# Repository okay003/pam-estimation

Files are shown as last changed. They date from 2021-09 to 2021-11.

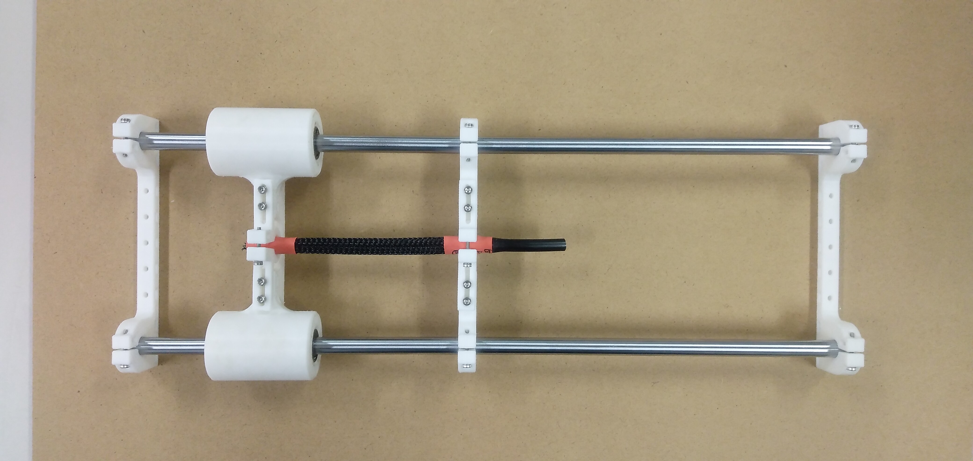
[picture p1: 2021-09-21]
overview.jpg

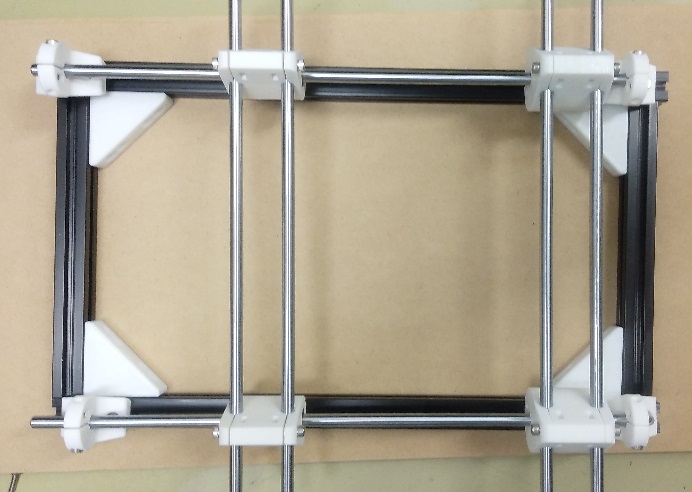
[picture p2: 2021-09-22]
temp state.jpg

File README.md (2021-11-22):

# pam-estimation

空気圧人工筋肉（PAM）を評価するための設備です。  
圧力を入力、その際の変位と収縮力を出力として計測します。  

概観
overview

試作版
oldsys

PAMの吸排気端を固定し、自由端が軸方向に直線的に収縮できるよう、リニアベアリング付きのガイドを配置してあります。  
計測のメインターゲットである変位はレーザ変位計VL53L0Xを用いて計測し、ArduinoとProcessingを介してPCでデータ処理を行います。  
収縮力は重りを用いて計測します。  
重りによる収縮力の計測は分解能が低く、システムによっては評価として不十分となるため、将来的にはエアシリンダ等を用いて負荷を連続的に制御できるようにします。  

研究で必要になったため開発しています。  

### BOM
・4本　任意長のアルミフレーム（ミスミ 5シリーズ）  
・32個　M4アルミフレーム用ナット  
・32個　M4六角穴付ボルト  
・6本　M8シャフト（アルミフレームと同じ長さ）  
・2個　M8リニアベアリング  
・1個　レーザ変位計 VL53L0X  
・1個　Arduino UNO  
・1本　Arduino用USBケーブル  
・1台　処理用PC  
・コンプレッサ  
・制御弁  
・PAM  
・計測用の重り

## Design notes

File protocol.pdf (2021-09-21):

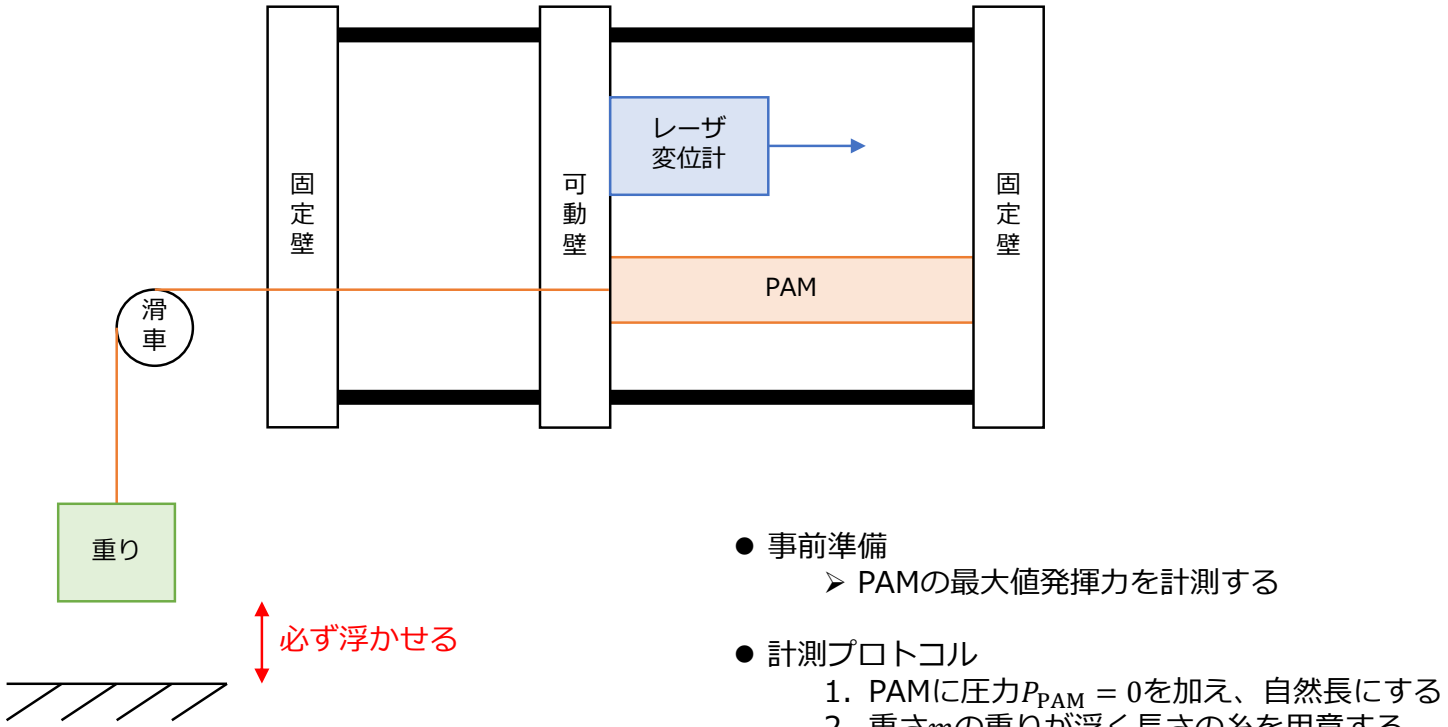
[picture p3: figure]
⚫ 事前準備 ➢ PAMの最大値発揮力を計測する; ⚫ 計測プロトコル 1. PAMに圧力PPAM = 0を加え、自然長にする; PAM; レーザ 変位計; 必ず浮かせる

2. 重さmの重りが浮く長さの糸を用意する
3. レーザ変位計が読んだ距離Lを計測する
4. PAMに圧力PPAMを加え、漸増させる（その結果、可動壁がPAMに牽引され移動する）
5. レーザ変位計が読んだ距離L

′を計測する
6. 圧力PPAMにおけるPAMの変位を、L − L

′より算出し、記録する
7. PAMに加える圧力PPAMを大まかに（1 [V]ずつ？）昇圧し、再度3.-10.を実行する
8. 実際に使いたい区間もしくは非線形性が著しい区間がある場合、 その区間に対してPAMに加える圧力PPAMを細かく（0.1 [V]ずつ？）昇圧し、再度3.-10.を実行 する
9. 重りの重さmを変更し、再度1.-8.を実行する 10.同規格のPAMや別規格のPAMに対して、再度1.-12.を実行する

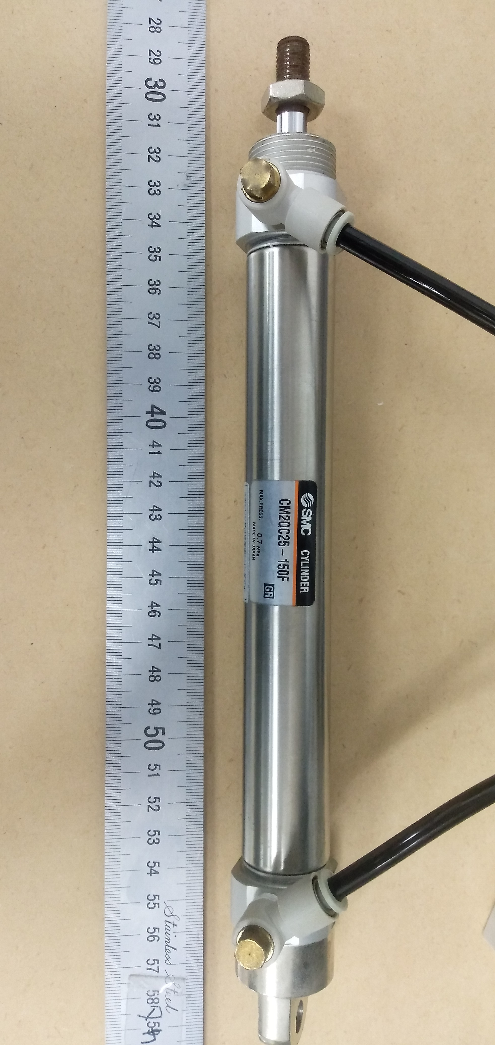
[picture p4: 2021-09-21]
aircylinder.jpg

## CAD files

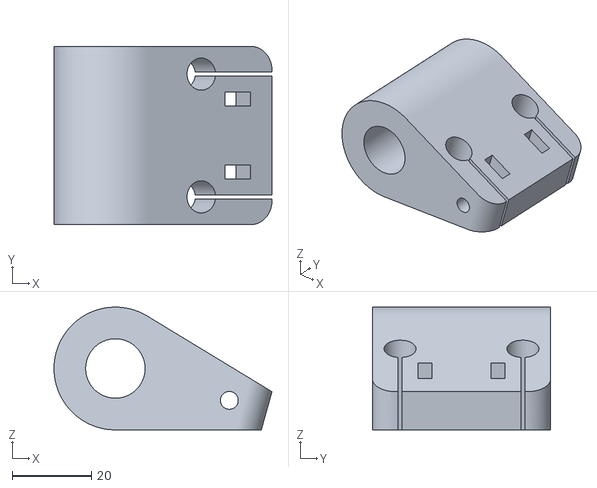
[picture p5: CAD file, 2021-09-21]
stl/slide holder.stl
55.0 x 45.0 x 31.0

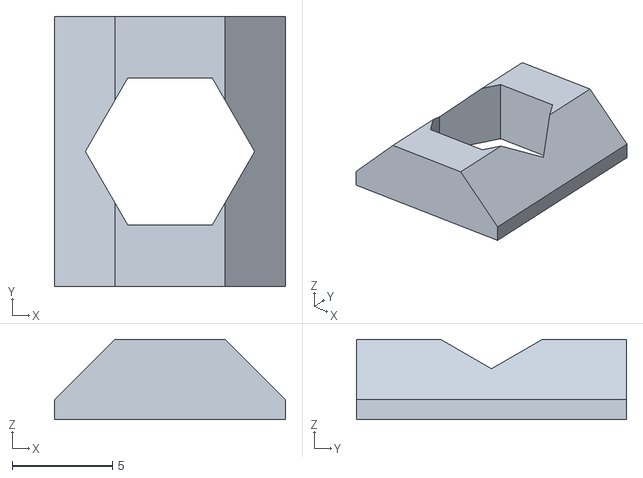
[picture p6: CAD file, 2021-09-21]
stl/key.stl
11.5 x 13.4 x 4.00

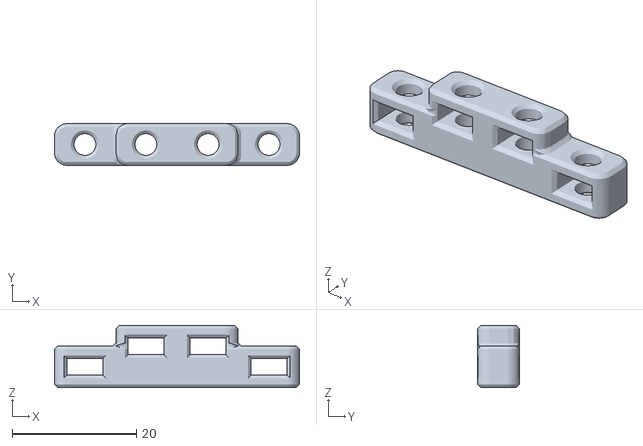
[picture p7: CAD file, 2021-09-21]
stl/vl53l0x holder.stl
39.4 x 6.70 x 10.0

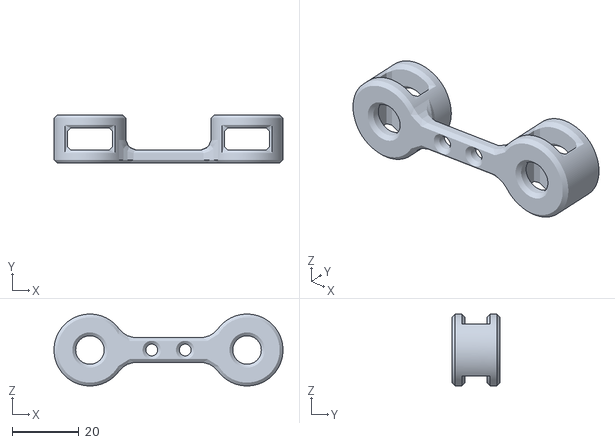
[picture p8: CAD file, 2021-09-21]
stl/vl53l0x calibratior.stl
68.5 x 14.5 x 21.5

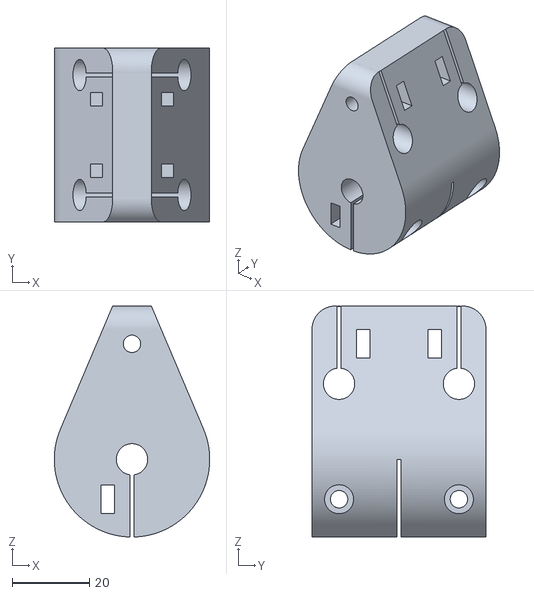
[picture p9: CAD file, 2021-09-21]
stl/hold holder.stl
40.2 x 45.0 x 59.8

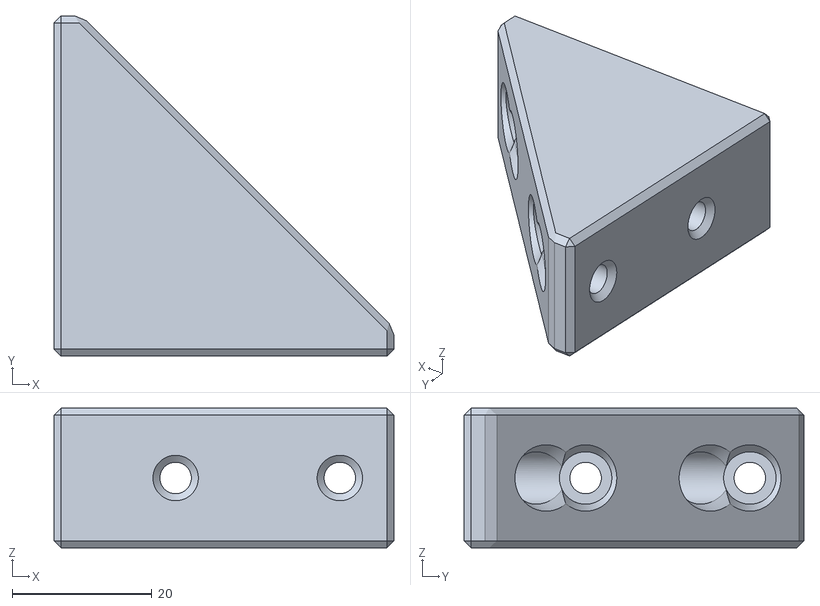
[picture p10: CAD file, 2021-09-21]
stl/elbow.stl
48.7 x 48.7 x 20.0

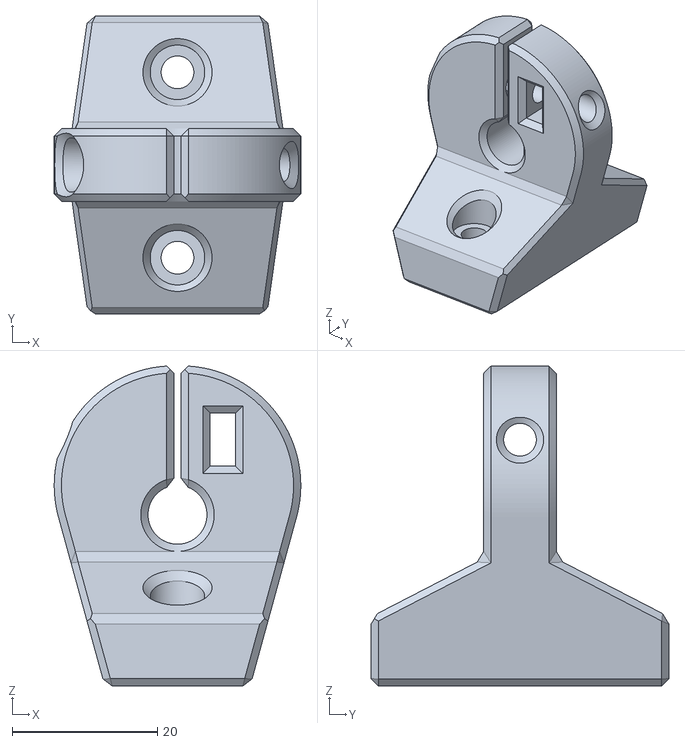
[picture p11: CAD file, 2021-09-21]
stl/shaft holder.stl
33.9 x 41.0 x 44.0

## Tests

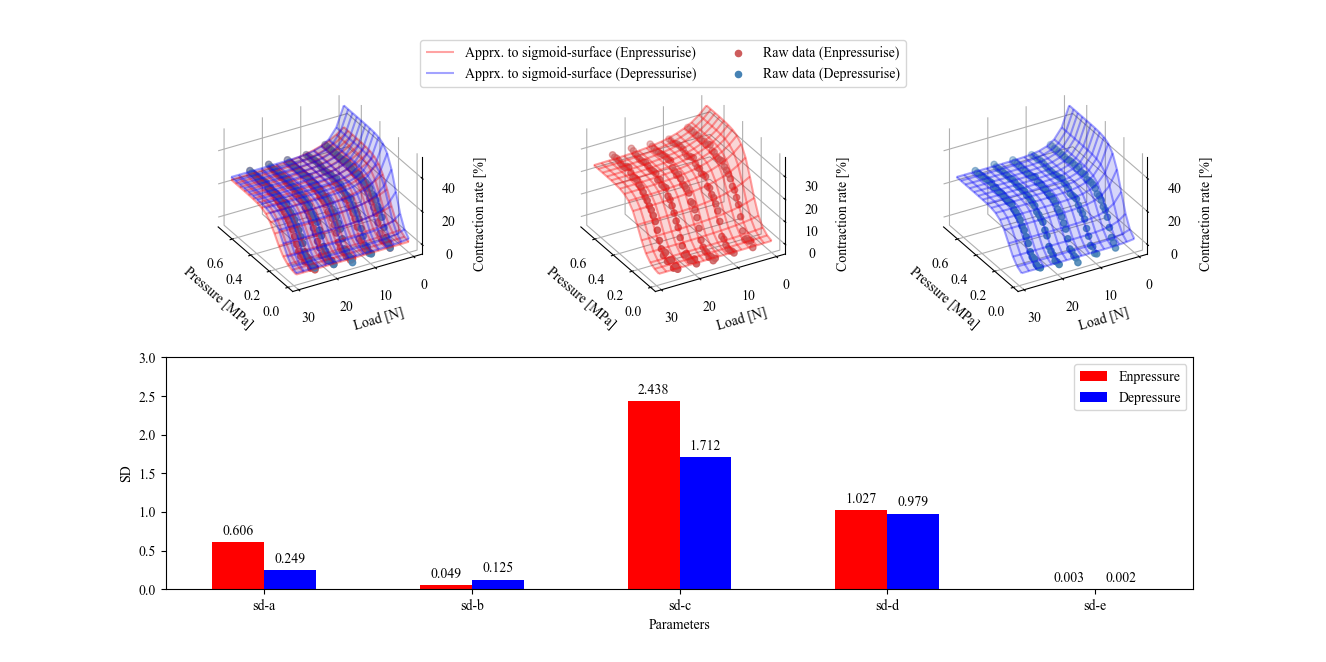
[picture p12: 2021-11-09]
fig/test.png

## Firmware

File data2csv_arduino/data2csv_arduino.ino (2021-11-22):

#include <VL53L0X.h>
#include <Wire.h>

VL53L0X sensor;
uint8_t MCP4725_ADDRESS = 0x60;  // mcp4725 address

// get distance data from VL53L0X
int getDistance();
// set DAC-out voltage
void setDac(uint16_t target);
// serial communication, send to processing
void scA2P(int index);
// wave initialize routine
void waveInitialize();
// wave finalize routine
void waveFinalize();

const String serialNumber = "MonoPlaE";  // default serialNumber is A
const int mass = 2500;  // default mass is 99 [g]
int eprVin = 0;  // default eprVin is 0
const int freeLength = 234;

float distanceAverage = 0;
int averageCounter = 0;

#define RISE_HOLD 0
#define RISE 1
#define FALL 2
#define FALL_HOLD 3
#define END 999
int waveState = RISE_HOLD;  // sequencer for PAM input
int waveCounter = 0;  // counter for PAM input

bool isFirst = true;

int stepNum = 1 << 5; // resolution of PAM input
int stepHeight = 4096 / stepNum; // PAM input value per step
unsigned long holdTimer = 0;  // timer of hold section
int holdTime = 8000; // length of hold section
int slope = 1; // speed of PAM input

void setup() {
  delay(4000);
  
  Serial.begin(9600);

  Wire.begin();
  sensor.setTimeout(500);
  if (!sensor.init()) {
    Serial.println("Failed to detect and initialize VL53L0X");
    while (1) {}
  }
  sensor.startContinuous();

  holdTimer = millis();
}

void loop() {
  setDac(eprVin);

  int cut = stepHeight * waveCounter - 1;
  if (waveCounter > stepNum) {
    cut = stepHeight * (2 * stepNum - waveCounter) - 1;
  }
  if (cut < 0) {
    cut = 0;
  }

  if (isFirst) {
    waveInitialize();
    isFirst = false;
  }

  switch (waveState) {
    case RISE_HOLD: // hold section (rise)
      if (millis() - holdTimer < holdTime) {
        if (waveCounter == 0) {
          eprVin = 0;
        } else {
          eprVin = cut;
        }
        distanceAverage += getDistance();
        averageCounter++;
      } else if (waveCounter == stepNum) {  // waveCounter gets turning point
        waveFinalize();
        waveState = FALL;
      } else {
        waveFinalize();
        waveState = RISE;
      }
      break;
    case RISE: // rise section
      if (eprVin < cut) {
        eprVin += slope;
        delay(10);
        if (eprVin > cut) {
          eprVin = cut;
        }
      } else {
        waveState = RISE_HOLD;
        holdTimer = millis();
      }
      break;
    case FALL_HOLD: // hold section (fall)
      if (millis() - holdTimer < holdTime) {
        eprVin = cut;
        distanceAverage += getDistance();
        averageCounter++;
      } else if (waveCounter == 2 * stepNum) {
        waveFinalize();
        waveState = END;
      } else {
        waveFinalize();
        waveState = FALL;
      }
      break;
    case FALL: // fall section
      if (eprVin > cut + 1) {
        eprVin -= slope;
        delay(10);
        if (eprVin < cut) {
          eprVin = cut;
        }
      } else {
        waveState = FALL_HOLD;
        holdTimer = millis();
      }
      break;
    case END: // end section
      scA2P();
      Serial.end();
      break;
    default:
      while (1) {
        Serial.println("error");
        delay(100);
      }
      break;
  }
  if (eprVin < 0) {
    eprVin = 0;
  }
}

// get distance data from VL53L0X
int getDistance() {
  int dist = sensor.readRangeContinuousMillimeters();
  if (sensor.timeoutOccurred()) {
    Serial.print("VL53L0X is timeouted");
  }
  return dist;
}

// set DAC-out voltage
void setDac(uint16_t target) {
  uint8_t low = target & 0xff;
  uint8_t high = (target >> 8) & 0x0f;

  Wire.beginTransmission(MCP4725_ADDRESS);
  Wire.write(high);
  Wire.write(low);
  Wire.endTransmission();
}

// serial communication, send to processing
void scA2P() {
  Serial.print("measurements:");  // watchword for communication
  Serial.print(serialNumber);
  Serial.print(',');
  Serial.print(freeLength);
  Serial.print(',');
  Serial.print(stepNum);
  Serial.print(',');
  Serial.print(mass);
  Serial.print(',');
  Serial.print(eprVin);
  Serial.print(',');
  Serial.print(distanceAverage);
  Serial.print('\n');
}

// wave initialize routine
void waveInitialize() {
  eprVin = 0;
  distanceAverage = 0;
  averageCounter = 0;
  scA2P();
  holdTimer = millis();
}

// wave finalize routine
void waveFinalize() {
  distanceAverage /= averageCounter;
  scA2P();
  distanceAverage = 0;
  averageCounter = 0;
  waveCounter++;
}
